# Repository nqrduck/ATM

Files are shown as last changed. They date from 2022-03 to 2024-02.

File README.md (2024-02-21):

# ATM (Automatic Tuning and Matching) System

## Automated Tuning and Matching

Tuning and Matching of the resonator coil is an essential part of Nuclear Quadrupole Resonance (NQR) spectroscopy. Because unknown samples are often scanned over large frequency ranges, Tuning and Matching has to be performed frequently. For high Q probe coils using mechanically trimmable capacitors, this is a long and tedious task.
To overcome this issue, an automatic Tuning and Matching system was developed using widely available low-cost components. Stepper drivers control mechanically trimmable capacitors and a microcontroller measures the Return Loss at resonance frequency. The system is capable of Tuning and Matching of a resonator coil in a frequency range from 75 to 125 MHz. It can also measure the Return Loss of the probe coil at its resonance frequency.

Additionally the system is capable of Tuning and Matching of NQR probe coils using varactor diodes. In this case the system can output a Tuning and Matching voltage in a range from 0 to 5V. 

This system is best used in combination with the [NQRduck](https://github.com/nqrduck) project which provides a graphical user interface for the ATM-system. Specifically, the [nqrduck-autotm](https://github.com/nqrduck/nqrduck-autotm) module is used to control the ATM-system.

The C++ program is then running on the ESP32 microcontroller. The NQRduck autotm module communicates with the ESP32 microcontroller using the USB interface.

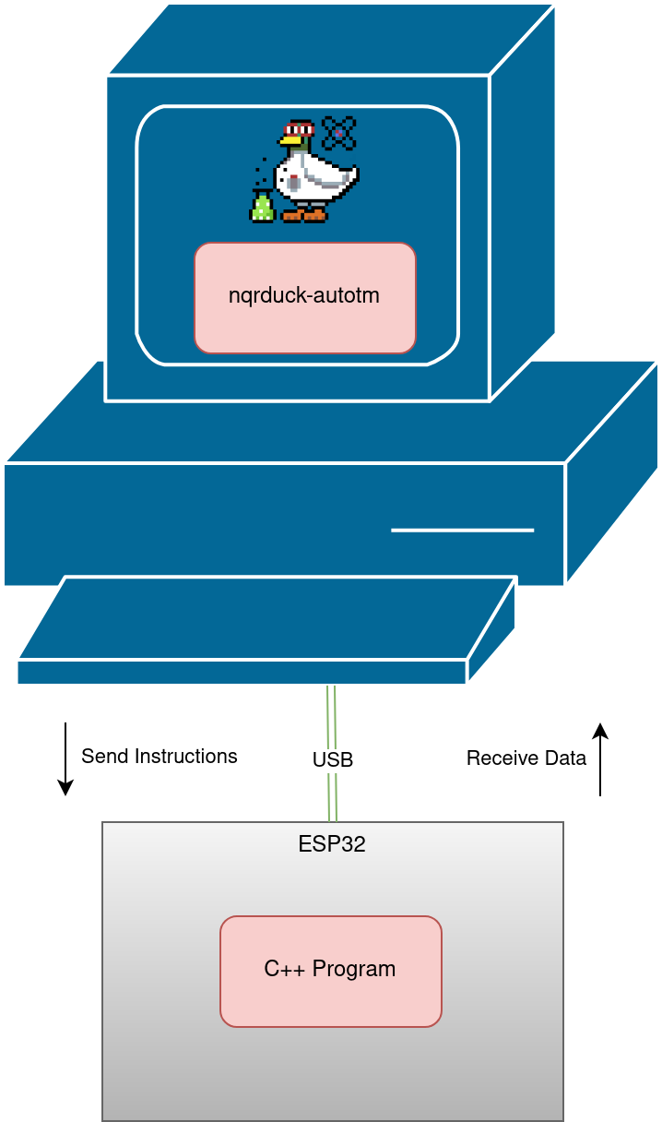
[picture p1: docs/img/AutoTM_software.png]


## Features
- Homing of the probe coil steppers using the sensorless load detection of TMC2130 stepper drivers. 
- A mechanically tunable probe coil can be tuned and matched in the frequency range of 75-125MHz.
- $S_{11}$ measurements can be performed at a frequency with a fixed position for the tuning and matching capacitors.
- Electrically tunable probe coils can be tuned and matched in the frequency range of 75-125MHz. 

## System overview
The ATM-system consists of multiple separate hardware components and multiple signal paths. One signal path is used to measure the reflection (characterized by the Return Loss) at a frequency with a fixed position for the tuning and matching capacitors. It is structured as following:

1.  A frequency synthesizer (ADF4351) outputs an RF signal to a filterbank. 
2. The filterbank filters out harmonic components of the frequency synthesizer's output.
3. The filtered signal is guided to a directional coupler setup. The directional coupler is connected to the resonator circuit and decouples the forward signal and the signal reflected at the resonator circuit. 
4. The forward and reflected signals are converted to a DC signal us an AD8302.
5. An ADC reads in the output of the AD8302 and calculates the Return Loss.

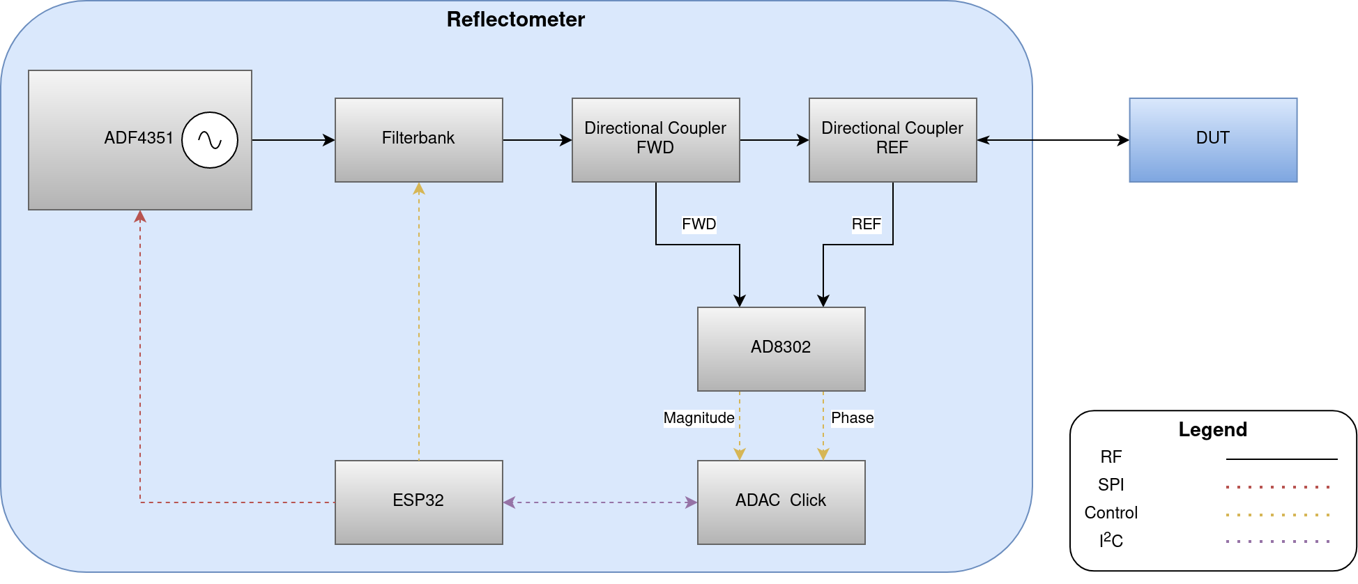
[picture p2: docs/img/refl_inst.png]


Since the system also needs to be able to adjust the mechanically trimmable capacitors, stepper motors have to be controlled.

1. A microcontroller sends commands to two stepper drivers using a Serial Peripheral Interface (SPI).
2. Those stepper drivers control the steppers which are mechanically coupled to the the tuning and matching capacitors of the probe coil.  

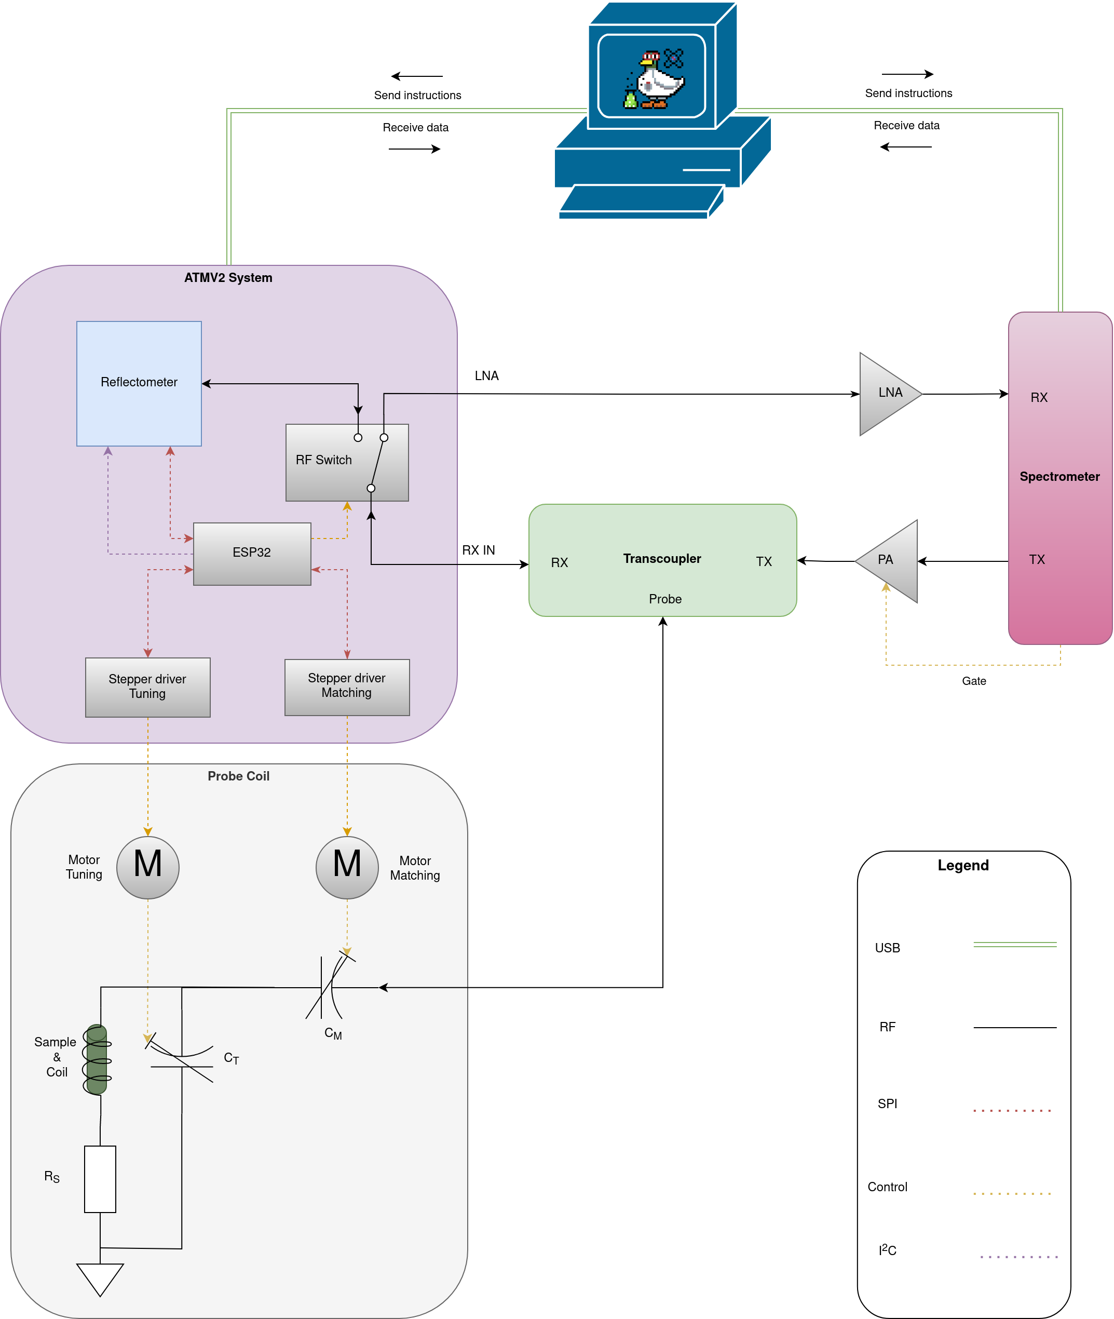
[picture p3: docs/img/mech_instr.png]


For electrically tunable probe coils the ESP32 uses the ADAC click to output a voltage to the varactor diodes.

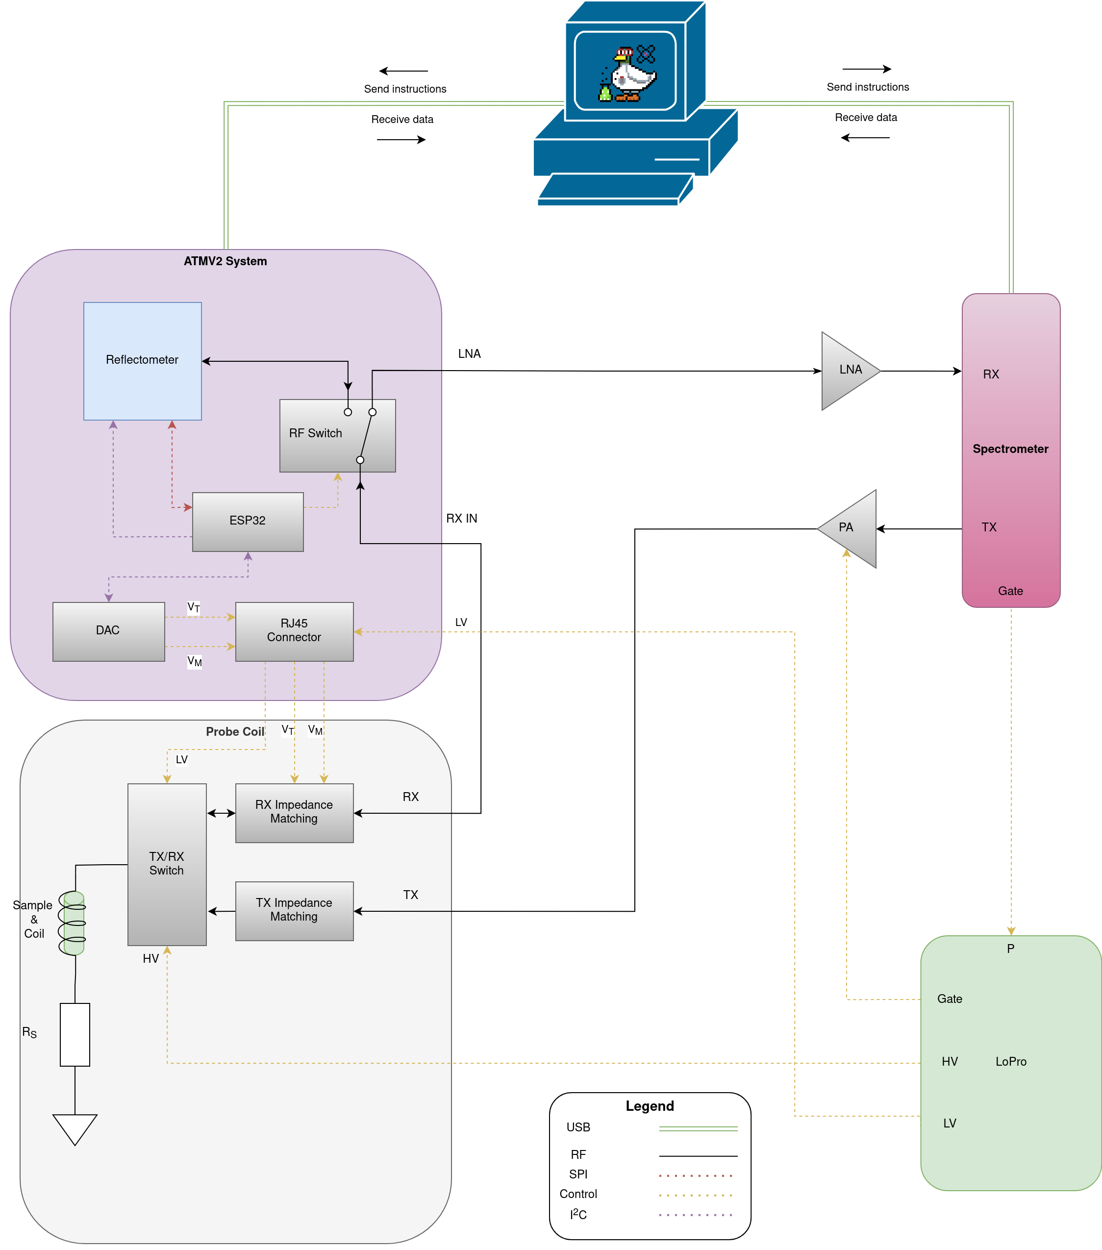
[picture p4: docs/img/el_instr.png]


## Hardware
Schematics for the electrical circuit and mechanical housing will be added soon. 

## Install instructions
1. Download the project as a zip file and import it as a platformio project. 
2. Connect your ESP32 microcontroller to your PC and flash the firmware onto it. 

For the installation of the NQRduck autoTM module please refer to the [NQRduck](https://github.com/nqrduck) documentation.

# Commands
The user can input different commands to the ATM-system using the serial interface of the ESP32. The general structure of such a command is a single character followed by a float value. The float value is only needed for certain commands.

# Results
A mechanically tunable probe coil was tuned and from 83MHz to 87MHz with a step size of 0.1MHz. The resulting reflection coefficient was then measured using the VNA (ZVL3, Rohde & Schwarz, Munich, Germany). The measured values were plotted using Matplotlib.

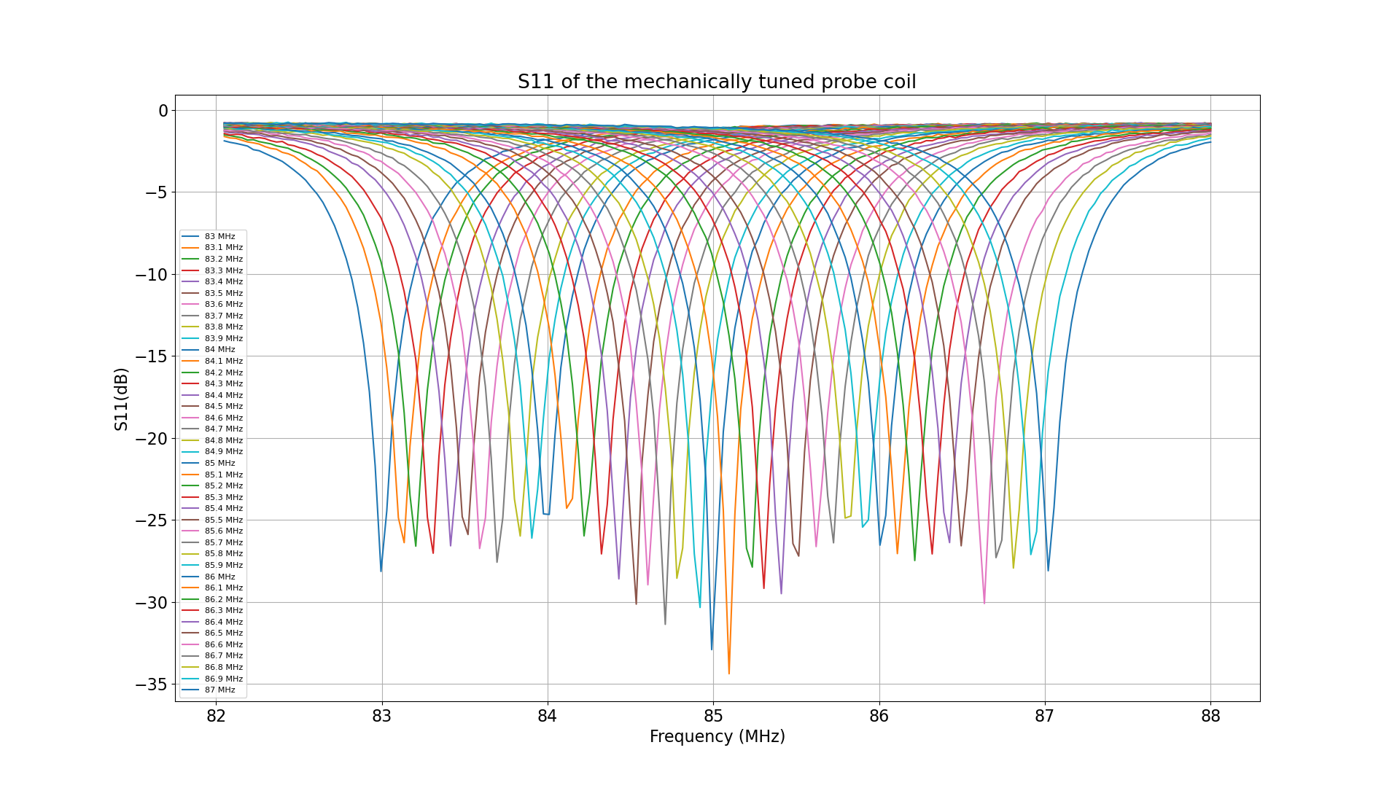
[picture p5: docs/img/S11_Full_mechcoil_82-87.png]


For the electrically tunable probe coil the probe coil was tuned and matched from 83 to 84MHz with a step size of 0.1MHz. The resulting reflection coefficient was then measured using the VNA (ZVL3, Rohde & Schwarz, Munich, Germany). The measured values were plotted using Matplotlib.

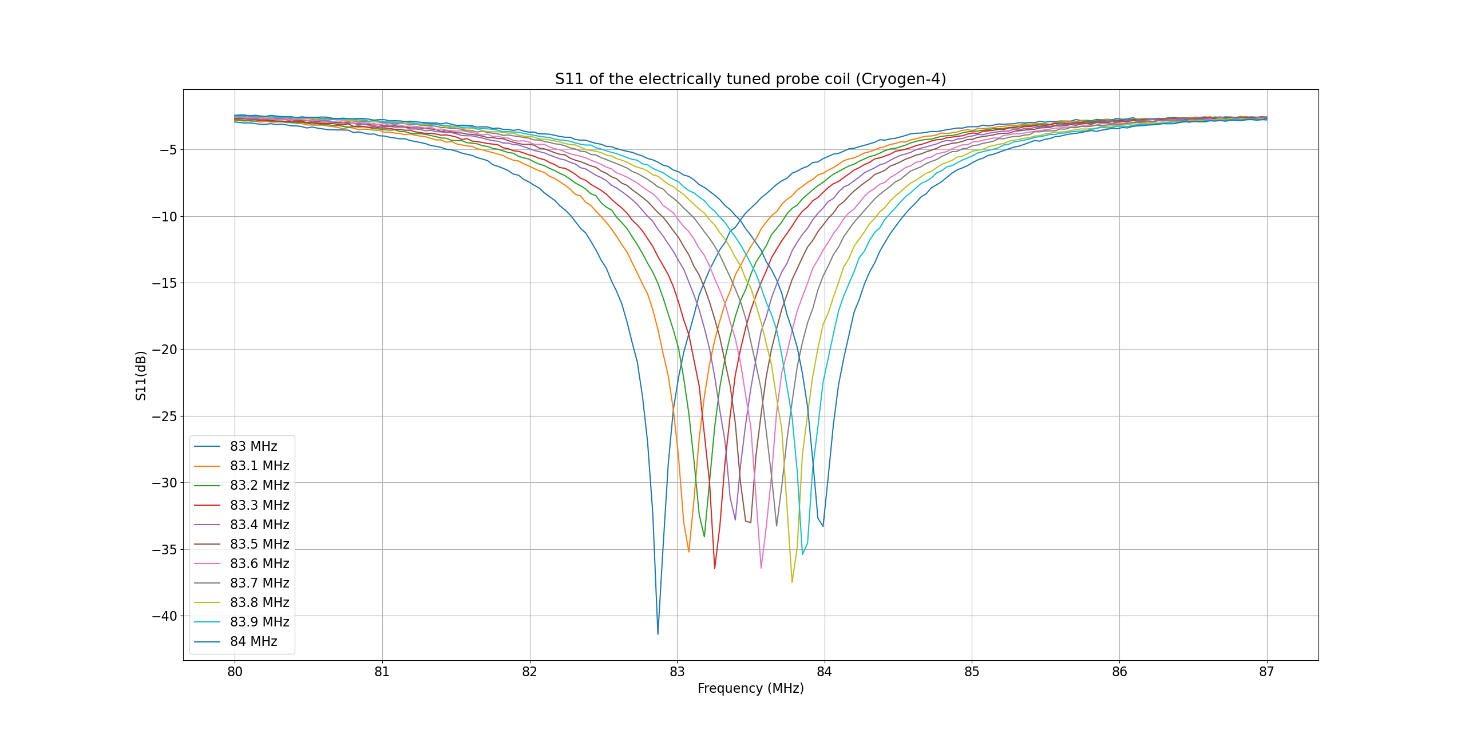
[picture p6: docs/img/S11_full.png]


## Future work
- Optimization for $S_{11}$ measurements. Right now the maximum achievable matching is about -25dB.
- Improve the calibration for $S_{11}$ measurements. Right now the setup is very impractical. 

## References
- [adf4351](https://github.com/dfannin/adf4351) by David Fannin was modified to be used with an ESP32 microcontroller. 
- [TMC2130Stepper](https://github.com/teemuatlut/TMC2130Stepper) by teemuatlut was used for the TMC2130 Stepper drivers.
- [AD5593R](https://github.com/LukasJanavicius/AD5593R-Arduino-ESP32-Library) by LukasJanavicius was used for the AD5593R ADC.
- [ArduiTaM](https://doi.org/10.5194/mr-1-105-2020) by Jouda et al. was an inspiration for the implementation.

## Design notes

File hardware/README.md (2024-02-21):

# Notes
These files are out of date and are not used in the current version of the ATM. I will update this documentation soon (hopefully).

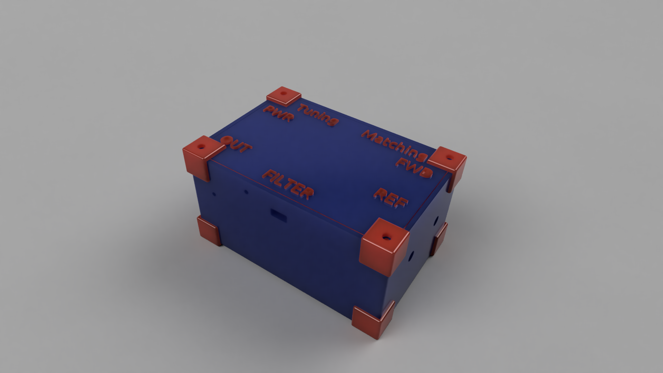
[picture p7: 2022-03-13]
hardware/CAD/housing_rendering.png

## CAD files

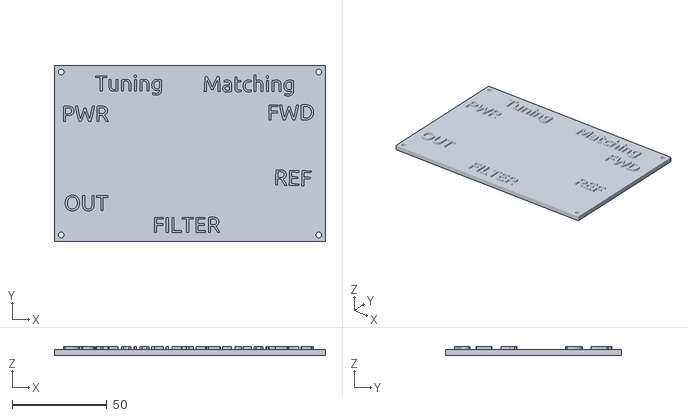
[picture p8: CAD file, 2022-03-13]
hardware/CAD/housing_top.stl
143.0 x 93.0 x 4.50

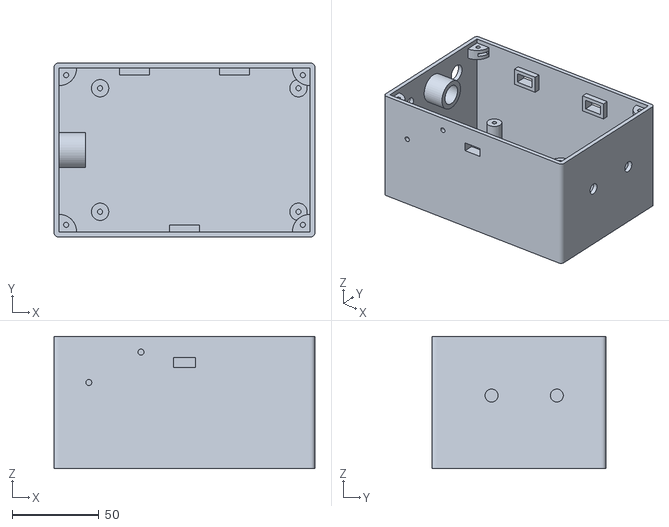
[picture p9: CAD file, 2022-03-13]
hardware/CAD/housing_base.stl
150.0 x 100.0 x 76.0

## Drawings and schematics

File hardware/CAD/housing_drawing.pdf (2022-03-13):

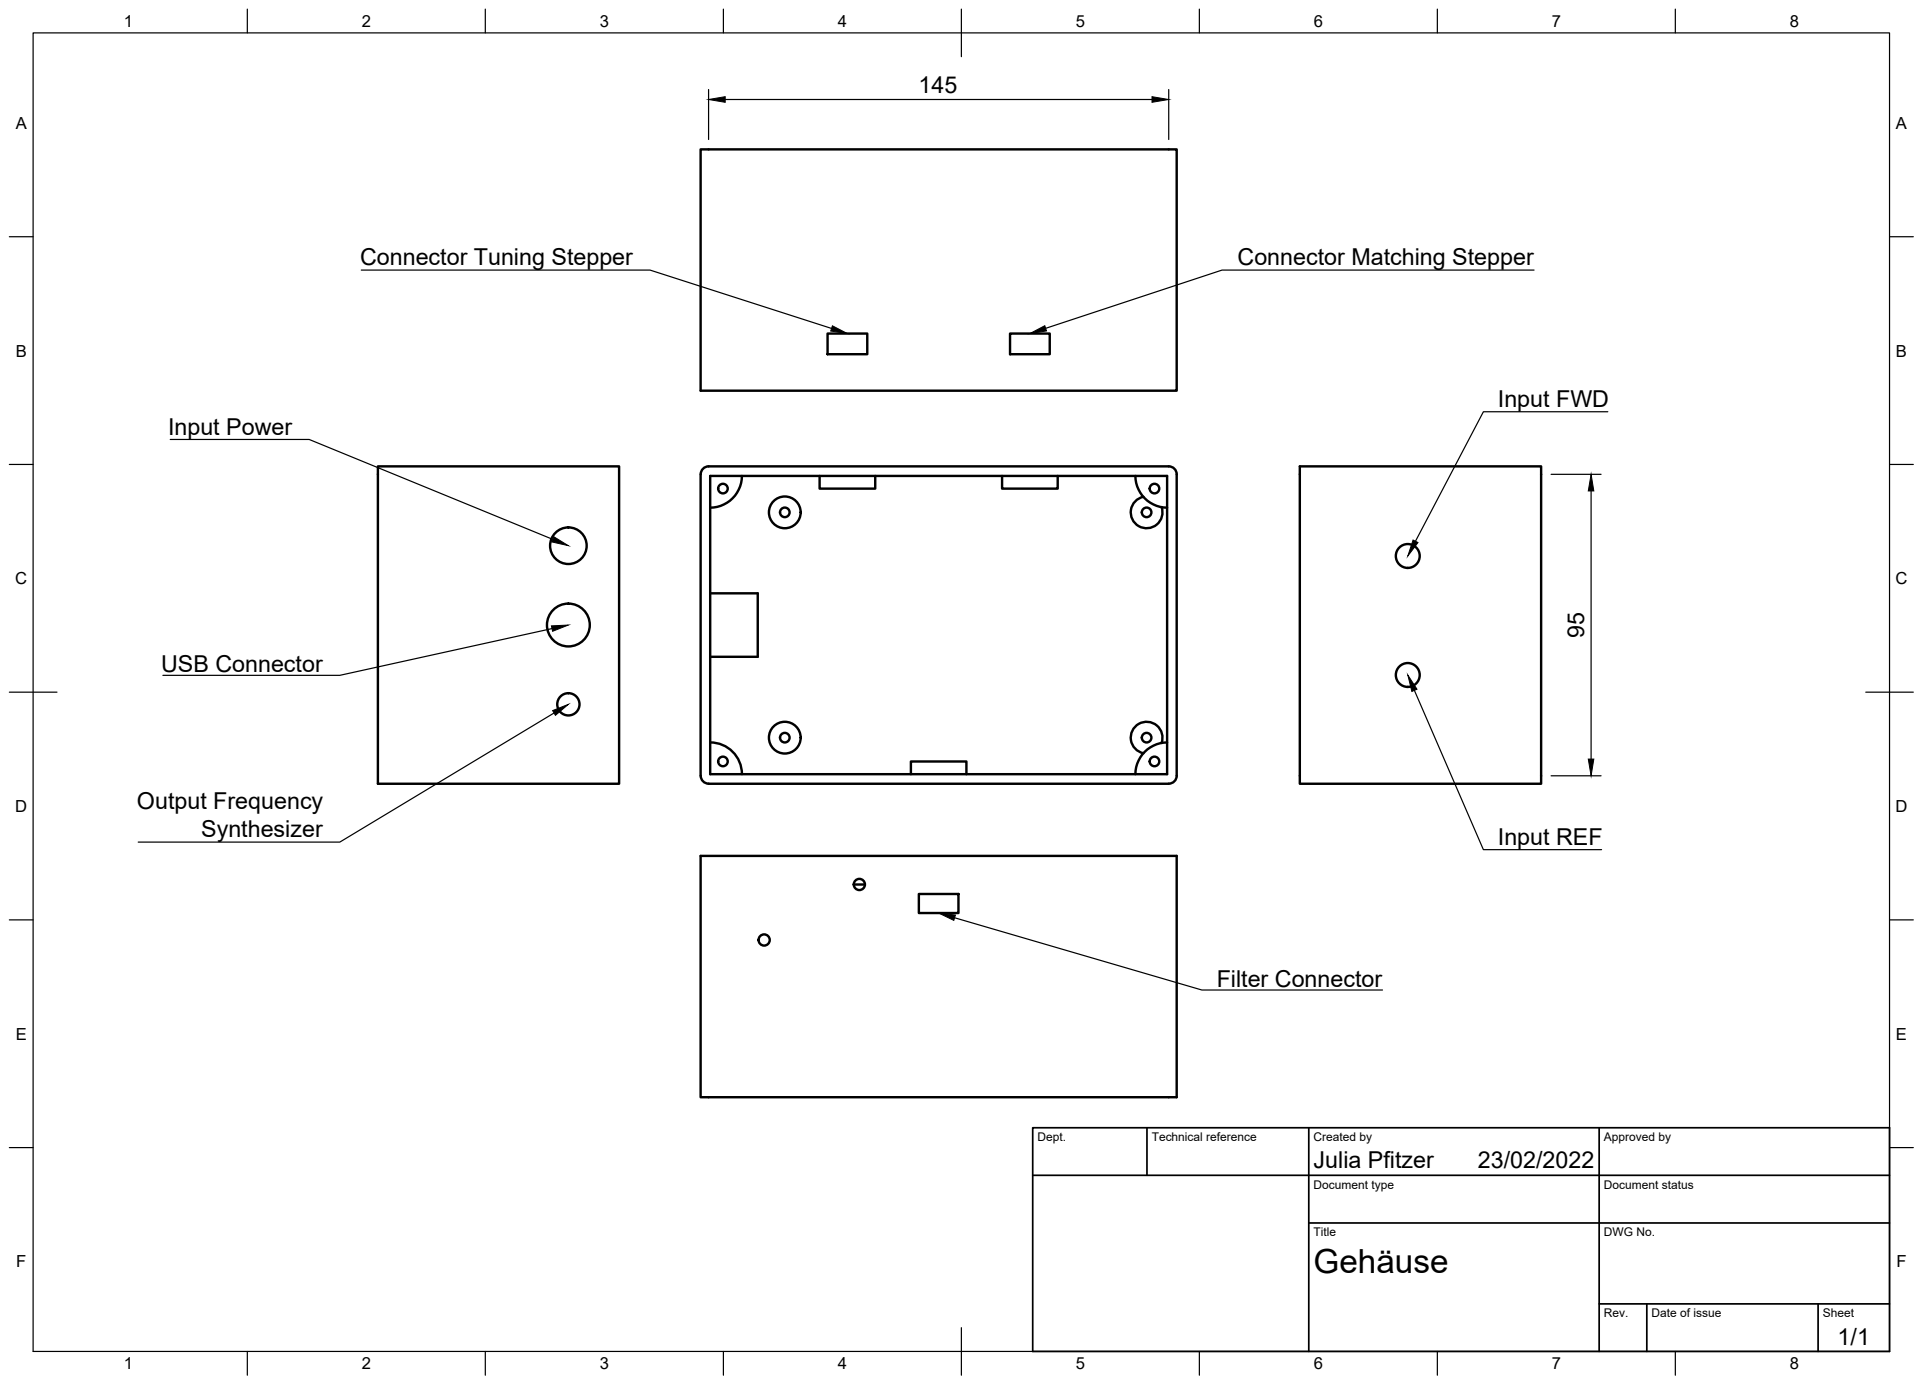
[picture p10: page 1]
Title; DWG No.; Rev.; Date of issue; Sheet; Input FWD; Input REF; Filter Connector; Input Power; Output Frequency; USB Connector; Connector Tuning Stepper; Connector Matching Stepper

Dept. | Technical reference | Created by Julia Pfitzer 23/02/2022 | Approved by

Document type | Document status

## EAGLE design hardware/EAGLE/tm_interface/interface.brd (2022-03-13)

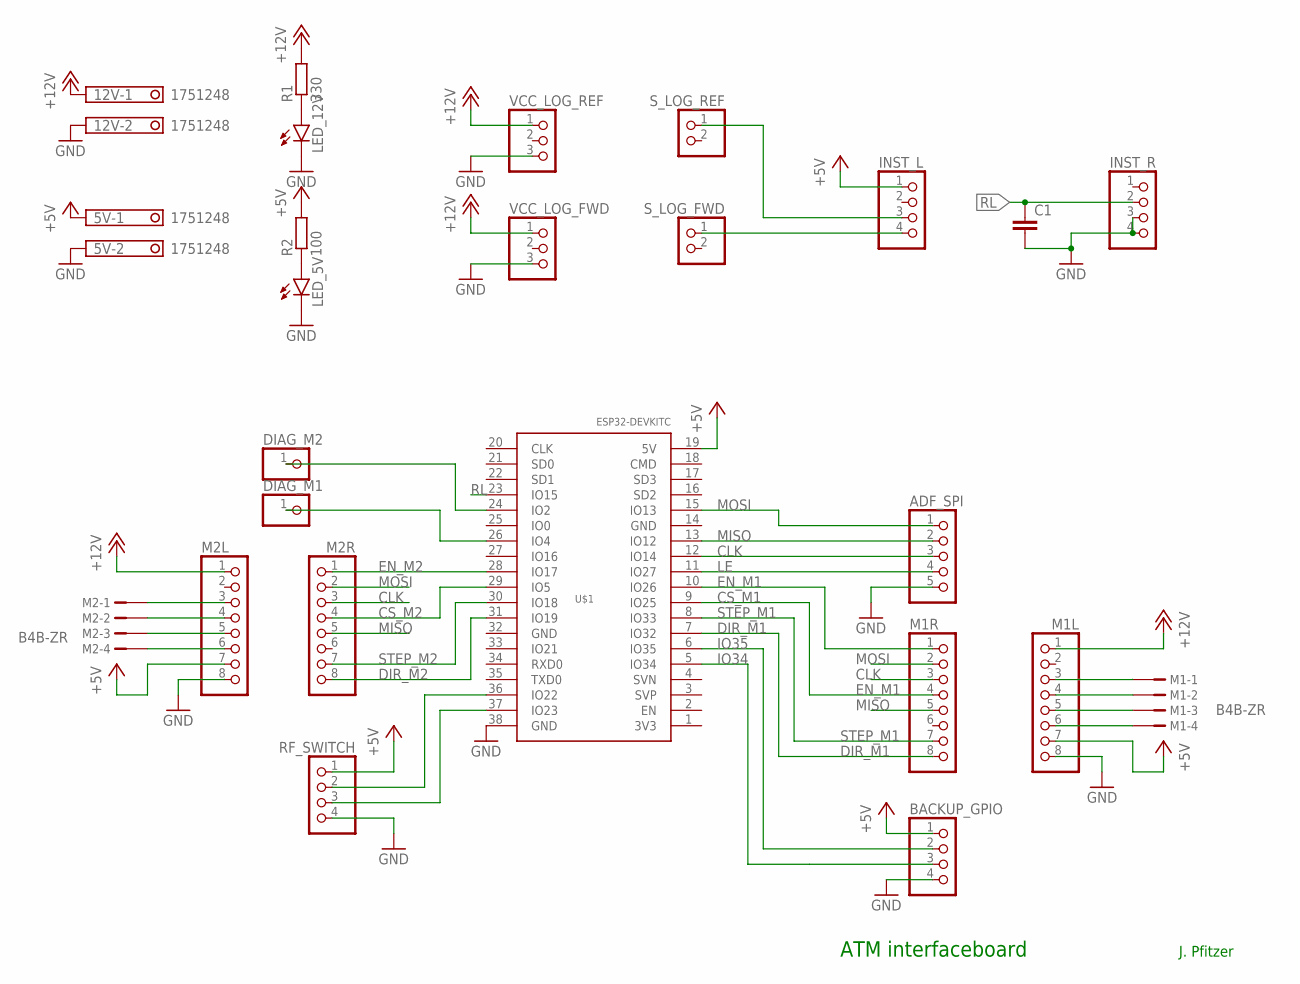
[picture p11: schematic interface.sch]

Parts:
5V, 12V: 1751248
ADF_SPI: PINHD-1X5; 1X05
BACKUP_GPIO: PINHD-1X4; 1X04
C1: C-EU025-025X050; C025-025X050
DIAG_M1, DIAG_M2: PINHD-1X1; 1X01
INST_L: PINHD-1X4; 1X04
INST_R: PINHD-1X4; 1X04
LED_5V, LED_12V: LED5MM
M1, M2: B4B-ZR
M1L, M1R, M2L, M2R: PINHD-1X8; 1X08
R1: 330; 0207/12
R2: 100; 0207/12
RF_SWITCH: PINHD-1X4; 1X04
S_LOG_FWD: PINHD-1X2; 1X02
S_LOG_REF: PINHD-1X2; 1X02
U$1: ESP32DEVKITC; ESP32-DEVKITC
VCC_LOG_FWD: PINHD-1X3; 1X03
VCC_LOG_REF: PINHD-1X3; 1X03

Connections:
+5V: 5V.1, BACKUP_GPIO.1, INST_L.1, M1L.7, M2L.7, R2.2, RF_SWITCH.1, U$1.19 (5V)
+12V: 12V.1, M1L.1, M2L.1, R1.2, VCC_LOG_FWD.1, VCC_LOG_REF.1
CLK: ADF_SPI.3, M1R.3, M2R.3, U$1.12 (IO14)
CS_M1: M1R.4, U$1.9 (IO25)
CS_M2: M2R.4, U$1.29 (IO5)
DIR_M1: M1R.8, U$1.7 (IO32)
DIR_M2: M2R.8, U$1.31 (IO19)
EN_M1: M1R.1, U$1.10 (IO26)
EN_M2: M2R.1, U$1.28 (IO17)
GND: 5V.2, 12V.2, ADF_SPI.5, BACKUP_GPIO.4, C1.2, INST_R.3, INST_R.4, LED_5V.K (C), LED_12V.K (C), M1L.8, M2L.8, RF_SWITCH.4, U$1.38 (GND), VCC_LOG_FWD.3, VCC_LOG_REF.3
IO34: BACKUP_GPIO.3, U$1.5 (IO34)
IO35: BACKUP_GPIO.2, U$1.6 (IO35)
LE: ADF_SPI.4, U$1.11 (IO27)
MISO: ADF_SPI.2, M1R.5, M2R.5, U$1.13 (IO12)
MOSI: ADF_SPI.1, M1R.2, M2R.2, U$1.15 (IO13)
unnamed: M1.1, M1L.3
unnamed: M1.2, M1L.4
unnamed: M1.3, M1L.5
unnamed: M1.4, M1L.6
unnamed: M2.1, M2L.3
unnamed: M2.2, M2L.4
unnamed: M2.3, M2L.5
unnamed: M2.4, M2L.6
unnamed: DIAG_M1.1, U$1.26 (IO4)
unnamed: DIAG_M2.1, U$1.24 (IO2)
unnamed: INST_L.3, S_LOG_REF.1
unnamed: INST_L.4, S_LOG_FWD.1
unnamed: RF_SWITCH.2, U$1.36 (IO22)
unnamed: RF_SWITCH.3, U$1.37 (IO23)
unnamed: LED_12V.A, R1.1
unnamed: LED_5V.A, R2.1
RL: C1.1, INST_R.2, U$1.23 (IO15)
STEP_M1: M1R.7, U$1.8 (IO33)
STEP_M2: M2R.7, U$1.30 (IO18)

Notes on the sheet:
ATM interfaceboard
J. Pfitzer

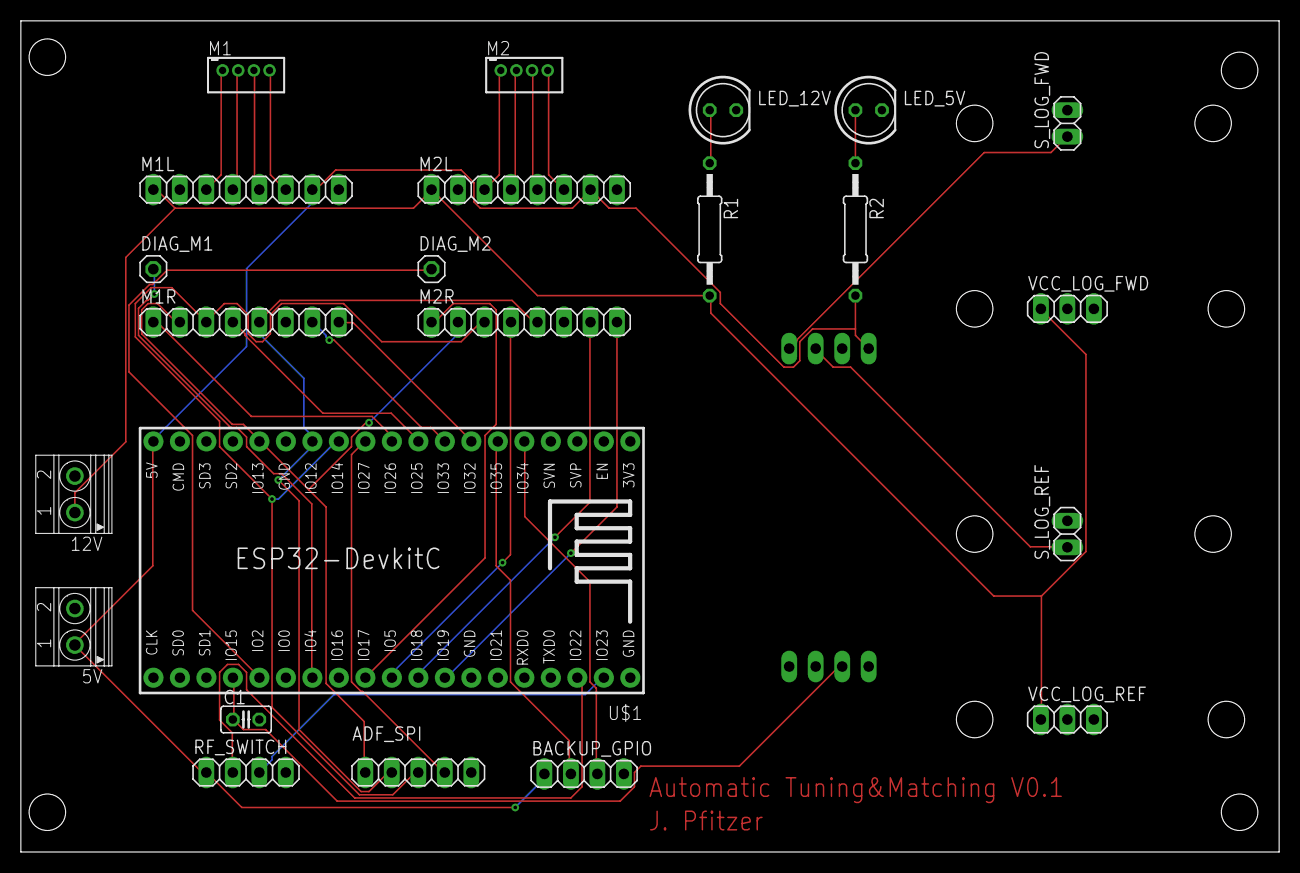
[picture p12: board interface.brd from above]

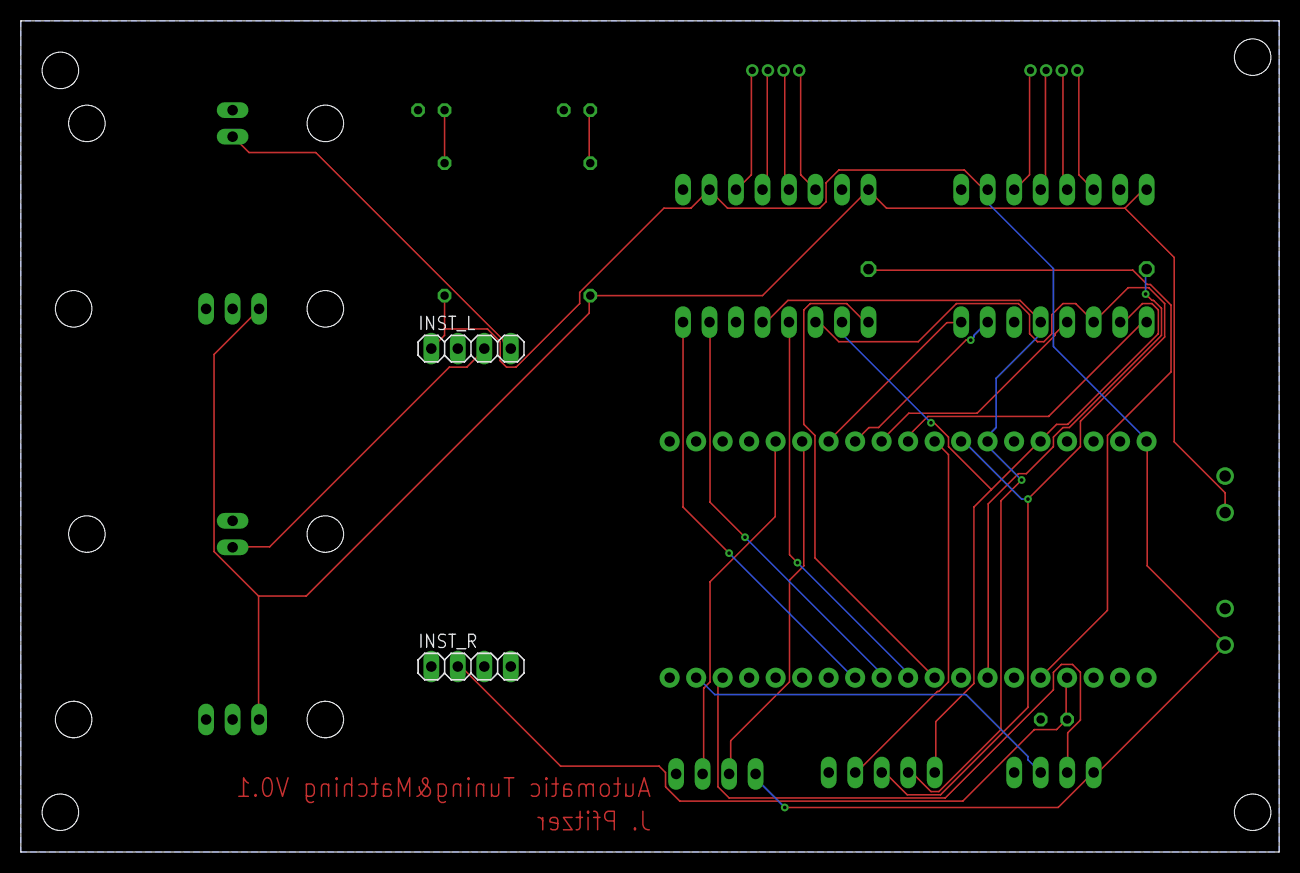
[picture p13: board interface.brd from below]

Board: 2 copper layers, 120.6 x 79.7 mm, 25 parts (2 on the bottom side), 34 nets.

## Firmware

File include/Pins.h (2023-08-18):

//SPI Pins
#define SCLK_PIN 14
#define MOSI_PIN 13
#define MISO_PIN 12

// I^2C Pins - ADC/DAC Module
#define I2C_SDA 21
#define I2C_SCL 16

//ADF Pins
#define LE_PIN 27
#define CE_PIN 25

// Pins M1
#define EN_PIN_M1    26  
#define DIR_PIN_M1   32  
#define STEP_PIN_M1  33  
#define CS_PIN_M1    25  

#define DIAG1_PIN_M1 4 // used for homing 

// Pins M2
#define EN_PIN_M2    17  
#define DIR_PIN_M2   19  
#define STEP_PIN_M2  18  
#define CS_PIN_M2    5 

#define DIAG1_PIN_M2 2 // used for homing

// Filter Bank
#define FILTER_SWITCH_A 23
#define FILTER_SWITCH_B 22

// RF Switch
#define RF_SWITCH_PIN 15

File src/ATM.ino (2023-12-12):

#include "global.h"

#include "CommandManager.h"
#include "commands/FrequencySweep.h"
#include "commands/TuneMatch.h"
#include "commands/Homing.h"
#include "commands/SetVoltages.h"
#include "commands/MeasureReflection.h"
#include "commands/VoltageSweep.h"
#include "commands/ControlSwitch.h"
#include "commands/MoveStepper.h"
#include "commands/PositionSweep.h"

#define DEBUG

#include "Debug.h"

CommandManager commandManager;

// Commands
FrequencySweep frequencySweep;
TuneMatch tuneMatch;
Homing homing;
SetVoltages setVoltages;
MeasureReflection measureReflection;
VoltageSweep voltageSweep;
ControlSwitch controlSwitch;
MoveStepper moveStepper;
PositionSweep positionSweep;

// Frequency Settings
#define FREQUENCY_STEP 100000U    // 100kHz frequency steps for initial frequency sweep
#define START_FREQUENCY 50000000U // 50MHz
#define STOP_FREQUENCY 110000000  // 110MHz

ADF4351 adf4351(SCLK_PIN, MOSI_PIN, LE_PIN, CE_PIN); // declares object PLL of type ADF4351

TMC2130Stepper tuning_driver = TMC2130Stepper(EN_PIN_M1, DIR_PIN_M1, STEP_PIN_M1, CS_PIN_M1, MOSI_PIN, MISO_PIN, SCLK_PIN);
TMC2130Stepper matching_driver = TMC2130Stepper(EN_PIN_M2, DIR_PIN_M2, STEP_PIN_M2, CS_PIN_M2, MOSI_PIN, MISO_PIN, SCLK_PIN);

AccelStepper tuning_stepper = AccelStepper(tuning_stepper.DRIVER, STEP_PIN_M1, DIR_PIN_M1);
AccelStepper matching_stepper = AccelStepper(matching_stepper.DRIVER, STEP_PIN_M2, DIR_PIN_M2);

Stepper tuner = {tuning_stepper, tuning_driver, DIAG1_PIN_M1, "Tuner"};

Stepper matcher = {matching_stepper, matching_driver, DIAG1_PIN_M2, "Matcher"};

// ADC DAC Module

AD5593R adac = AD5593R(23, I2C_SDA, I2C_SCL);
bool DACs[8] = {0, 0, 1, 1, 0, 0, 0, 0};
bool ADCs[8] = {1, 1, 0, 0, 0, 0, 0, 0};

// This sets the active filter to the first one in the list
Filter active_filter = FILTERS[0];

boolean homed = false;

void setup()
{
  Serial.begin(115200);

  // Here the commands are registered
  commandManager.registerCommand('f', &frequencySweep);
  commandManager.registerCommand('d', &tuneMatch);
  commandManager.registerCommand('h', &homing);
  commandManager.registerCommand('v', &setVoltages);
  commandManager.registerCommand('r', &measureReflection);
  commandManager.registerCommand('s', &voltageSweep);
  commandManager.registerCommand('c', &controlSwitch);
  commandManager.registerCommand('m', &moveStepper);
  commandManager.registerCommand('p', &positionSweep);

  pinMode(MISO_PIN, INPUT_PULLUP); // Seems to be necessary for SPI to work

  // Setup fo the tuning stepper
  tuner.DRIVER.begin();          // Initiate pins
  tuner.DRIVER.rms_current(400); // Set stepper current to 400mA.
  tuner.DRIVER.microsteps(16);
  tuner.DRIVER.coolstep_min_speed(0xFFFFF); // 20bit max - needs to be set for stallguard
  tuner.DRIVER.diag1_stall(1);
  tuner.DRIVER.diag1_active_high(1);
  tuner.DRIVER.sg_stall_value(STALL_VALUE);
  tuner.DRIVER.shaft_dir(0);
  tuner.DRIVER.stealthChop(1); // Enable extremely quiet stepping

  pinMode(DIAG1_PIN_M1, INPUT);

  // Setup fo the matching stepper
  matcher.DRIVER.begin();          // Initiate pins and registeries
  matcher.DRIVER.rms_current(200); // Set stepper current to 200mA. The command is the same as command TMC2130.setCurrent(600, 0.11, 0.5);
  matcher.DRIVER.microsteps(16);
  matcher.DRIVER.coolstep_min_speed(0xFFFFF); // 20bit max - needs to be set for stallguard
  matcher.DRIVER.diag1_stall(1);
  matcher.DRIVER.diag1_active_high(1);
  matcher.DRIVER.sg_stall_value(STALL_VALUE-2);
  matcher.DRIVER.shaft_dir(0);
  matcher.DRIVER.stealthChop(1); // Enable extremely quiet stepping

  digitalWrite(EN_PIN_M1, LOW);
  digitalWrite(EN_PIN_M2, LOW);

  tuner.STEPPER.setMaxSpeed(12000);
  tuner.STEPPER.setAcceleration(12000);
  tuner.STEPPER.setEnablePin(EN_PIN_M1);
  tuner.STEPPER.setPinsInverted(true, false, true);
  tuner.STEPPER.enableOutputs();

  matcher.STEPPER.setMaxSpeed(12000);
  matcher.STEPPER.setAcceleration(12000);
  matcher.STEPPER.setEnablePin(EN_PIN_M2);
  matcher.STEPPER.setPinsInverted(true, false, true);
  matcher.STEPPER.enableOutputs();

  tuner.STEPPER.setCurrentPosition(0);

  matcher.STEPPER.setCurrentPosition(0);

  // Setup for the ADF4351 frequency synthesizer
  adf4351.begin();

  adf4351.setrf(25000000U);
  adf4351.pwrlevel = 2; // This equals 2dBm*/ For the electrical probe coils one should use at least -20dbm so an attenuator is necessary
  adf4351.setf(START_FREQUENCY);

  // Setup for the RF Switch for the filterbank
  pinMode(FILTER_SWITCH_A, OUTPUT);
  pinMode(FILTER_SWITCH_B, OUTPUT);

  digitalWrite(FILTER_SWITCH_A, LOW);
  digitalWrite(FILTER_SWITCH_B, HIGH);

  // ADAC module
  adac.enable_internal_Vref();
  adac.set_DAC_max_2x_Vref();
  adac.set_ADC_max_2x_Vref();
  adac.configure_DACs(DACs);
  adac.write_DAC(VM, 0.0);
  adac.write_DAC(VT, 0.0);

  adac.configure_ADCs(ADCs);
}


void loop()
{
  // Serial communication via USB.
  // Commands:
  // f<start frequency>f<stop frequency>f<frequency step> - Frequency Sweep
  // d<target frequency in MHz>f<start frequency>f<stop frequency>f<frequency step> - Tune and Match
  // h - Homing
  // v<VM voltage in V>v<VT voltage in V> - Set Voltages
  // r<frequency in MHz> - Measure Reflection
  // s<start voltage in V>s<stop voltage in V>s<voltage step in V> - Voltage Sweep
  // c<filter identifier> - Control Switch for the filterbank 'p' stands for preamplifier and 'a' for automatic tuning and matching. 
  // m<stepper identifier><steps> - Move stepper motor. 't' for tuner and 'm' for matcher. Positive steps move the stepper away from the motor and negative steps move the stepper towards the motor.
  // p<tuning range in steps>t<tuning step in steps>t<tuning backlash in steps>m<matching range in steps>m<matching step in steps>m<matching backlash in steps> - Position Sweep
  if (Serial.available())
  {
    String input_line = Serial.readStringUntil('\n'); // read string until newline character

    char command = input_line.charAt(0); // gets first character of input

    commandManager.executeCommand(command, input_line);
    commandManager.printCommandResult(command);
    /*
    Optimize matching call
    else if (command == 'm')
    {
      printInfo("Optimize Matching around frequency:");
      uint32_t resonance_frequency = findCurrentResonanceFrequency(START_FREQUENCY, STOP_FREQUENCY, FREQUENCY_STEP);

      printInfo(resonance_frequency);

      optimizeMatching(resonance_frequency);

      // calculate sum
    }
    else if (command == 's')
    {

      float frequency_MHz = input_line.substring(1).toFloat();
      uint32_t frequency = validateInput(frequency_MHz);
      if (frequency == 0)
        return;

      int sum = sumReflectionAroundFrequency(frequency);
      printInfo("For frequency:");
      printInfo(frequency);
      printInfo("Sum of the reflection is:");
      printInfo(sum);

      // Calibration Call
    }
    else if (command == 'c')
    {
      printInfo("Calibrating ...");
      getCalibrationValues();
    } */
  }
}

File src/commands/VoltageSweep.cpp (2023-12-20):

#include "Utilities.h"
#include "VoltageSweep.h"

void VoltageSweep::execute(String input_line)
{
    // Command format is s<frequency in MHz>o<optional tuning voltage>o<optional matching voltage>


    // First we get the frequency where the voltage sweep should be performed
    char identifier = 's';
    char delimiter = 'o';
    int frequencyIndex = input_line.indexOf(identifier) + 1;

    // Check if optional voltages are given
    if (input_line.indexOf(delimiter, frequencyIndex) == -1)
    {
        // If no optional voltages are given, we perform an automatic voltage sweep
        String frequency_MHz = input_line.substring(frequencyIndex);
        uint32_t frequency = validateInput(frequency_MHz.toFloat());
        if (frequency == 0)
        {
            printInfo("Invalid frequency input for voltage sweep.");
            return;
        }
        printInfo("Starting automatic voltage sweep at " + String(frequency) + " MHz");

        automaticSweep(frequency);
        return;
    }
    else
    {
        // If optional voltages are given, we perform a voltage sweep with the given voltages
        int tuningIndex = input_line.indexOf(delimiter, frequencyIndex) + 1;
        int matchingIndex = input_line.indexOf(delimiter, tuningIndex) + 1;

        float frequency_MHz = input_line.substring(frequencyIndex, tuningIndex - 1).toFloat();
        float tuning_voltage_predefined = input_line.substring(tuningIndex, matchingIndex - 1).toFloat();
        float matching_voltage_predefined = input_line.substring(matchingIndex).toFloat();

        uint32_t frequency = validateInput(frequency_MHz);
        if (frequency == 0)
        {
            printInfo("Invalid frequency input for voltage sweep.");
            return;
        }
        printInfo("Starting preset voltage sweep at " + String(frequency) + " MHz" + " with tuning voltage " + String(tuning_voltage_predefined) + " V and matching voltage " + String(matching_voltage_predefined) + " V");
        presetVoltages(frequency, tuning_voltage_predefined, matching_voltage_predefined);
    }
}

void VoltageSweep::presetVoltages(uint32_t frequency, float_t tuning_voltage_predefined, float_t matching_voltage_predefined)
{
    // For preset voltages we only scan the tuning and matching voltages in a reduced range. This is because the voltages are already close to the optimum values.
    float_t TUNING_RANGE = 0.2;
    float_t MATCHING_RANGE = 0.2;
    float_t voltage_step = 0.01;

    setFrequency(frequency);

    float_t tuning_voltage_start = tuning_voltage_predefined - TUNING_RANGE;
    if (tuning_voltage_start < 0.0)
        tuning_voltage_start = 0.0;

    float_t tuning_voltage_stop = tuning_voltage_predefined + TUNING_RANGE;
    if (tuning_voltage_stop > 5.0)
        tuning_voltage_stop = 5.0;

    printInfo("Tuning voltage start: " + String(tuning_voltage_start));

    float_t matching_voltage_start = matching_voltage_predefined - MATCHING_RANGE;
    if (matching_voltage_start < 0.0)
        matching_voltage_start = 0.0;

    float_t matching_voltage_stop = matching_voltage_predefined + MATCHING_RANGE;
    if (matching_voltage_stop > 5.0)
        matching_voltage_stop = 5.0;

    //  We use the sweepVoltages function to find the optimum tuning and matching voltages
    sweepVoltages(voltage_step, tuning_voltage_start, tuning_voltage_stop, matching_voltage_start, matching_voltage_stop);

    adac.write_DAC(VM, matching_voltage);
    adac.write_DAC(VT, tuning_voltage);
}

void VoltageSweep::automaticSweep(uint32_t frequency)
{
    float MAX_VOLTAGE = 5.0;
    float MIN_VOLTAGE = 0.0;

    // First set the frequency 2 MHz below the target frequency
    uint32_t distance = 2000000;
    setFrequency(frequency - distance);

    // Then we perform a rough voltage sweep with a step size of 1V
    sweepVoltages(1, MIN_VOLTAGE, MAX_VOLTAGE, MIN_VOLTAGE, MAX_VOLTAGE);

    // Now we set the target frequency
    setFrequency(frequency);

    // Then we perform a more precise voltage sweep with a step size of 0.1V but only in the region of the found voltages
    float_t tuning_range = 0.5;
    sweepVoltages(0.05, tuning_voltage - tuning_range, tuning_voltage + tuning_range, MIN_VOLTAGE, MAX_VOLTAGE);

    // Then we perform a last very precise voltage sweep with a step size of 0.01V but only in the region of the found voltages
    tuning_range = 0.1;
    float_t matching_range = 0.2;
    sweepVoltages(0.01, tuning_voltage - tuning_range, tuning_voltage + tuning_range, matching_voltage - matching_range, matching_voltage + matching_range);

    if (tuning_voltage < 0.0 || matching_voltage < 0.0)
    {
        tuning_voltage = 0.0;
        matching_voltage = 0.0;
        printError("No valid voltages found for automatic voltage sweep.");
    }

    // Finally we set the found voltages
    adac.write_DAC(VM, matching_voltage);
    adac.write_DAC(VT, tuning_voltage);
}

void VoltageSweep::sweepVoltages(float_t voltage_step, float_t tuning_start, float_t tuning_stop, float_t matching_start, float_t matching_stop)
{
    int AVERAGES = 4;
    // We want to maximize the reflection value, so we start with zero
    float_t minimum_reflection = 0.0;

    // This bruteforces the optimum voltage for tuning and matching.
    for (float_t c_tuning_voltage = tuning_start; c_tuning_voltage <= tuning_stop; c_tuning_voltage += voltage_step)
    {
        for (float_t c_matching_voltage = matching_start; c_matching_voltage <= matching_stop; c_matching_voltage += voltage_step)
        {
            // Set the tuning and matching voltage
            adac.write_DAC(VT, c_tuning_voltage);
            adac.write_DAC(VM, c_matching_voltage);

            // Measure the reflection at the given frequency
            int reflection = readReflection(AVERAGES);

            // If the reflection is lower than the current minimum, we have found a new minimum
            if (reflection > minimum_reflection)
            {
                minimum_reflection = reflection;
                tuning_voltage = c_tuning_voltage;
                matching_voltage = c_matching_voltage;
                // If the returnloss is better than 14dB, we can stop the voltage sweep
                // float_t reflection_db = (reflection - 900) / 30.0;
                // if (reflection_db > 14)
                //    return;
            }
        }
    }
}

void VoltageSweep::printResult()
{
    // Print the results which are then read by the autotm module
    char identifier = 'v';
    char delimiter = 't';

    String text = String(identifier) + String(tuning_voltage) + String(delimiter) + String(matching_voltage);

    Serial.println(text);
}

void VoltageSweep::printHelp()
{
    Serial.println("Voltage sweep command");
    Serial.println("Syntax: v<frequency in MHz>");
    Serial.println("Example: v100");
    Serial.println("This will perform a voltage sweep at 100 MHz and will return the optimum tuning and matching voltages for this frequency.");
}

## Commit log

2022-01-06 Changed Stepper definitions.
2022-02-08 Changed power level for improved matching.
2022-02-09 Implemented capacitor loading for improved resonance search
2022-02-10 Implemented frequency-ranges with filterbank.
2022-02-14 Changed filter selection to default frequency range.
2022-02-17 Updated pins for interface-board.
2022-02-21 Major improvement to matching. Changed Filterbank pins.
2022-03-13 Added hardware files
    [housing_base.stl, housing_top.stl, interface.brd, interface.sch]
2023-08-16 Implemented basic voltage sweep.
2023-08-17 Improved voltage sweep.
2023-08-18 Updated RF switch PIN.
2023-08-18 Added argument for printing of data.
2023-08-18 Improved switching of filters.
2023-12-07 Fixed bug which lead to negative voltages.
2023-12-08 Added position update to stepper movement.
2023-12-10 Improved stepper stalling
2023-12-15 Implemented preset voltage sweep and returning of set voltages for tuning and matching.
2023-12-15 Removed pritning of voltages text.
2023-12-16 Fixed mixing up of tuning and matching voltages ...
2023-12-20 Updated voltage sweep.
2024-02-21 Updated docs to reflect the current implementation.
